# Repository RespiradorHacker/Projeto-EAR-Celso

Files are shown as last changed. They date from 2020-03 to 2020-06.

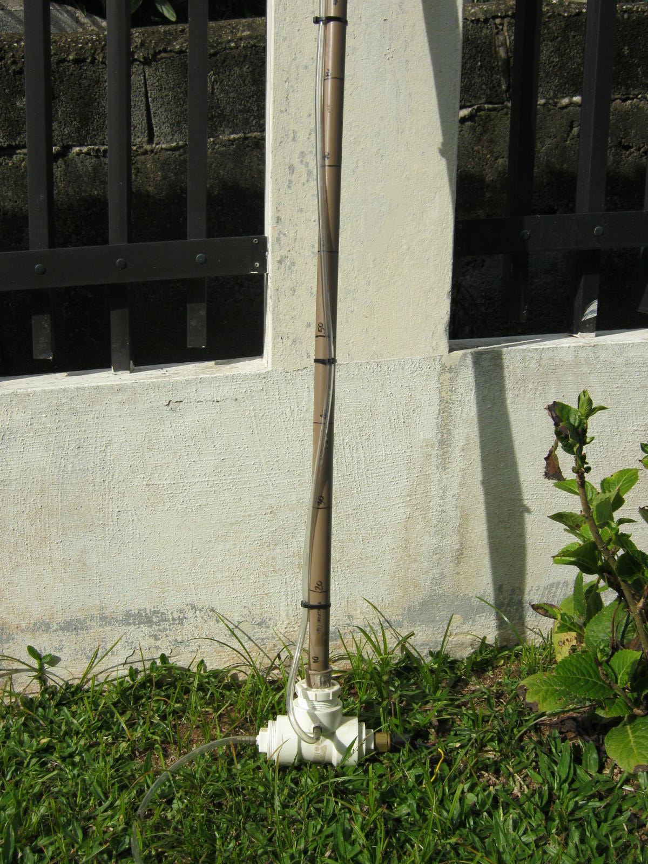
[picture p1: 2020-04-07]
PhotosAndVideos/200407 09.00 Px Sensor Calibration.JPG

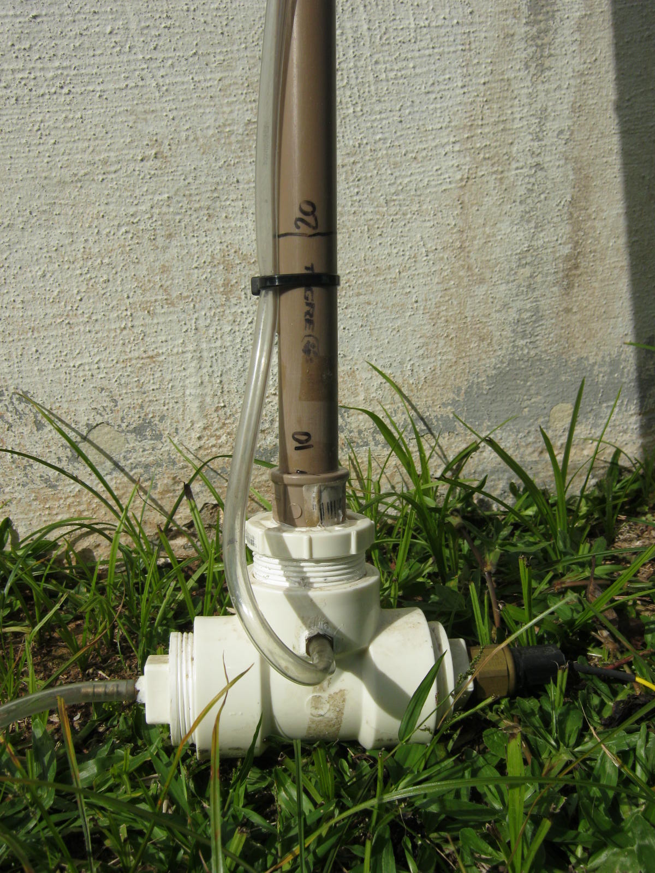
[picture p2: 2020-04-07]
PhotosAndVideos/200407 09.00 Px Sensor Calibration Detail.JPG

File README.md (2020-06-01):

# e-AR (EAR) PROJECT - EMERGENCY VENTILATOR
This project was born because of CoVid19 pandemic.
The project Goal is to provide an emergency ventilator system to help CoVid19 serious cases using locally available resources. eAR was designed to meet specifications according to MHRA (UK) - Rapidly Manufactured Ventilator System and inspired by MIT E-Vent (USA) concepts and specs.

This is an OPEN HARDWARE - OPEN SOURCE PROJECT. 

DISCLAIMER: we will NOT take any responsability on devices built using partial or total information from this project. 
Any device used for life support and medical applications must meet all local requirements and they must be homologated by local regulatory agencies in ANY case.

The target is to run an entire ventilation system using an automotive car battery and an O2 can.
The initial project leader is Celso Ken Mori Monteiro, automotive designer with +30 yrs experience on automotive embedded systems
as OEM designer for customers as GM, Ford, VW, Fiat, Mercedes Benz, Scania, Navistar, Marcopolo, Agco...

The technology for first PCBs was downsized due to components availability in emerging countries so distributed production could be achieved even in small brazilian towns. The electronic parts are:
- PTH components
- Single-sided PCB, obtainable even by DIYs. 

Besides inclusive concept there is also a FR4 SMT version available for volume production.

Basic concepts:
- External FIO2 O2 + AIR mixer based on timed mechanical truck air valves and plastic bag container
- AMBU smasher based on car window motor due to availabilty and great mechanical characteristics. Motor reversion is necessary to allow dinamic changes of BPM, Tidal Volume, pressure ramping, I/E Ratio and Plateau Hold Time without ANY mechanical change.
- ECU based on Arduino Pro Mini (the most available in emerging countries) and SPI based IO expension
- 2 motor drive options: relay (need second adjustable supply or buck) and PWM driven mosfet driver

Project Evolution:
- full HW schematics and system component's description available on "EAR System Developer's HW Guide", portuguese only version
- PCB Gerbers available, Single Side PTH version, Motor driver on relay option only. Time and size were underestimated because we no longer use these old technologies. Released on March 30, 2020.
- Mech prototype phase 2 aproved, torque is OK and current is low.
- Gerbers of single sided boards on PTH components published on March 30, 2020. Time and size were underestimated because we no longer use these old technologies. 
- EAR System Developer's SW Guide released on March 30, 2020.
- Functional electronics prototype built and delivered on April 2, 2020. No changes in PCBs are necessary except hardware end-of-courses provided for EAR ECU Motor Driver Board. Test driven by firmware FW00 - focused on HW testing only. Reads input pots, control motor with reversal action, measures motor current and tests IO expansion board. All items are functional.
- FW00 published in April 3, 2020.
- Added Mosfet-based PWM Motor Driver and Absolute position sensor using a car fuel level sensor.
- First working mechanical+electrical prototype delivered in April 6, 2020.
- Added Pressure Sensor in April 7, 2020. First artificial lung is a balloon so first pressure profile was obtained. It Sounds promising.
- Firmware controls Tidal Volume and BPM according to Set Potentiometers. First functional firmware produce variable pressure ramps as needed, FW met 8-30 BPM dynamic range specification.
- Added motor cutoff in inspiratory phase according to pressure preset on pot Overpressure Threshold within 1cm H20 resolution.
- Added full mechanical design for functional AMBU compressing ARM in April 11, 2020
- Added in April 12, 2020: Motor Driver, mosfet NN version. Full Kicad design with schematics, PCB and Gerbers.
- Added in April 12,2020: eAR External watchdog Timer to increase eAR reliability. Full Eagle design with schematics, PCB and Gerbers.
- Added in April 13,2020: I/E selection (1:1, 1:2, 1:3 and 1:4) and Plateau Hold Time selection (150, 250, 500 and 1000ms hold on Plateau)
- Added in April 13,2020: Gol G3 tank level float sensor added as absolute position sensor. Increased linearity, resolution and availability
- Mech proto 3.2 added ball bearing in compression arm, currently performing cycling tests
- Added in April 15,2020; eAR Pressure sensor Board Design and PCB, MPX5010DP supported
- Added in April 21,2020: 10x10cm FR4 SMT single PCB design for volume production, verified design, send to production
- Added in April 21,2020: Mechanical proto 3.2 drawings delivered, functional design
- April 30, 2004: eAR FR4 Single-Board PCBs arrived, courtesy from Digicart/SC
- May 1st, 2020: eAR system reached 14 days of 24/7 operation, with 403,412 beathing cycles completed. eAR met minimum durability MHRA (UK) Spec with a prototype built on MDF, a window lift BDC motor and a 20-yrs-old chevy tank float sensor
- May 5, 2020: Multiple pressure sensor added, allowing almost any kind of linear pressure sensor to be connected to eAR system, including MPX5010, MPX10 almost all versions and packages including MPVZ and MP3V and experimental ultra-low-cost MPS20N0040D-S sensor
- May 12, 2020: Integrated EAR ECU tested, functional test OK. Some minor drilling errors corrected, some improvements done and new PCB generated. New mosfet driver option added in firmware as needed. Some components changed values due to standardization effort to ease production. eAR electronics is ready for mass production.
- May 23, 2020: Added first steel based eAR mechanical design, by Ricardo Suzuki. Arm sensor changed to DS 1901 non-contact TPS. 
- June 1st, 2020: Added R2 of mechanical design in two verions, geared arm and 4-linked-bars by Ricardo Suzuki

Pending:
- Software reliability improvements.
- Assisted Ventilation Firmware on hold. It can delay ANVISA aproval when requested.

Special thanks to all people that made this project real!
It's impossible to list all names involved, I apologize for forgetting someone.
The partial list follows:

Project Contributors, as they have joined this project
- Joannes Berque (FR): first design idea.
- Celso Monteiro: eletronics and firmware design, system conception and documentation.
- Diego Padilha and Lucas Pianizzer: electronics and mechanical design+prototyping. 
- Marcelo Pires: electronic CAD, schematics capture & PCB Design.
- Nicolai Rutkevich: mechanical concepts.
- Bruno Afogliatto: decontamination concepts.
- Gustavo Ortenzi: motor drive alteratives.
- Ricardo Suzuki: system concepts and mechanical design.
- Rodrigo Azevedo: organized Github Project.
- Douglas Esteves: interface with other projects.
- João Cardoso and Leonardo Afonso: Kicad Capture for Open Hardware.
- Andre Novelli e Victor Acioly: AMBU bags replacement.
- Flavio Alves: GUI design
- David Loos: electronics assembly

References:
- MIT E-Vent: human requirements and system conception ideas.
- MHRA (UK) Rapidly Manufactured Ventilator System

Healthcare professionals involved:
- Angelica Mammana M.D. helped stablishing specs and performed crytical analysis.
- Fernando Machado M.D. was the first contributing doctor.
- Lucio Flavio M.D.
- Ana Teresa Gama.

Project supporters:
- Fabio Knihs.
- Norberto Tomio.
- Gabriel Casagrande.
- Ivandro Ceccato.

Thanks to my family, special thanks to my dear wife Tissa and my children Joana, Gustavo and Leonardo, for their unlimited support and to all the people that prayed for this project, and God that inspired and guided me all the time.

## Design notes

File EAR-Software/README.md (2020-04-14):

# e-AR (EAR).

Open-source Software that runs on e-AR Project MCU. 
- eAR was designed to meet specifications according to MIT E-Vent (USA) and MHRA (UK) - Rapidly Manufacuted Ventilator System.  
- Provides basic functions to human ventilation.
- Runs on e-AR Hardware, Arduino based, functionally available and published as Open Hardware.
- Always use the lastest available software, just download the folder and use Arduino IDE

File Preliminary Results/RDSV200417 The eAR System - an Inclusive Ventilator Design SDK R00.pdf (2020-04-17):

Doc.: RDSV200417 The eAR System - an Inclusive Ventilator Design SDK R00.doc | 1/11

_____________________________________________________________________________

| Data | Signatures
Author: Celso Monteiro | 17/04/2020 | | Títle: The eAR System – Ventilator SDK
Verif.:

Aprov.:

### 1. Scope

The scope of this document is to describe the creation of the eAR system. The eAR system is a low-cost SDK for inclusive ventilator systems developed in around 30 days during the CoVid19 pandemics by a self-funding voluntary multidisciplinary team in Brazil. We’ll present the design alternatives, choices, results and limitations, focused on AMBU automation. This is far from being the best system but it’s the best we can do now on what we have available.

All electronics hardware, mechanical, and software documents are available in open hardware, open software basis in the Githut https://github.com/RespiradorHacker/Projeto-EAR-Celso

This design can be changed at any moment without previous announcement.

Disclaimer: we have no responsability about any device built upon information from eAR project and we emphasize that devices must be built in strict compliance to local regulations, following expert recommendations and they must be homologated by local regulatory agencies.

### 2. Document Control

- April 17, 2020: Document emission R00

### 3. References

- Open Source COVID19 Medical Supplies facebook: https://www.facebook.com/groups/670932227050506/
- COVID-19 Air BRASIL - Fast production of assisted ventilation devices https://www.facebook.com/groups/235476464265909/
- RDSV200320 Emergency Automatic Respirator Specification R00 – Preliminary
- RDSV200322 EAR Hardware Proposition Draft R00 – PTBR
- RDSV200327 EAR Project Briefing PTBR R04
- MIT E-Vent – “Key Ventilation Specifications”
- MHRA (UK) Rapidly Manufactured Ventilator System

### 4. Abbreviations and Terms

- MIT: Massachusetts Institute of Technology (USA)
- MHRA: Medicines & Healthcare products Regulatory Agency (UK)

Doc.: RDSV200417 The eAR System - an Inclusive Ventilator Design SDK R00.doc | 2/11
- AMBU: in this scope is just a silicone bag
- BDC: Brushed Direct Current
- FIO2: Fraction of Inspired O2 defines proportion of O2 in inspired air
- ECU: Electronic Control Unit
- PEEP: Positive End Expiratory Pressure
- PTH: Plated Through Hole, electronics technology
- SPI: Serial Peripheral Interface
- WIP: Work in Progress
- SDK: system development kit

### 5. Design Reasons

There are several AMBU automation solutions, why do we need another one? All AMBU automation we could find are based on materials available in research labs. These materials were not found normally in emerging countries like Brazil and especially on the worldwide uprising of Covid19. Detours on purchasing are announced in a daily basis for all resources targeted to fight Covid19.

So eAR basic concept is creating a system that could be built using available components and local resources. It should be a possibility for any town, including small towns in emerging countries.

### 6. eAR Design - Hardware

The AMBU bag was the enriched air propeller chosen because it was available at all places, used by emergency medical care worldwide.

We needed something to compress the AMBU so at first we were considering an indirect compressed air based AMBU compressing device but this solution needed a dedicated chamber, more complicated to build and we considered that some small hospitals had few available spots of compressed air.

So we switched to electric motor possibilities. There are many alternatives that could do the job, we’ve considered NEMA type stepper motors, car windshield and car window motors. We had previous experience with all three motors. NEMA motors are the only brushless option, but we discarded because of availability in smaller towns. Windshield motors were discarded because they are power hungry, heavy and they were not built to reverse operation. We needed reversal because we wanted to control Tidal volume without mechanical changes. Car windows were the most available (up to 4 on each car and million cars spread through the country) and they had excess torque, low power consumption and reversal capability. There’s a life limit associated with this choice, although these motors work on worm gears and they have rubber couplers, they are brushed motors, and they wear. Due to low load condition we’ve estimated around 1 million cycles (to be confirmed). Possibly it’ll last longer than the AMBU.

Doc.: RDSV200417 The eAR System - an Inclusive Ventilator Design SDK R00.doc | 3/11

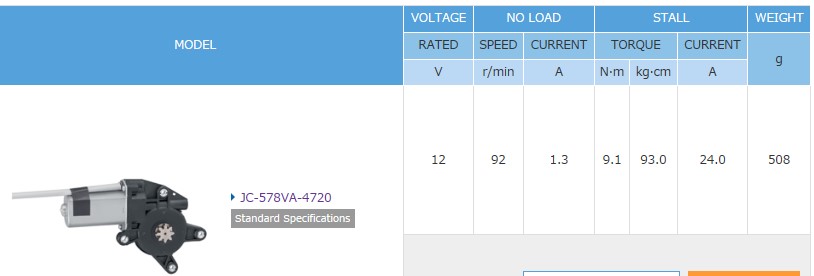
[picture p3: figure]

Motor used in eAR system

We’ve built mechanical prototype 1, it was similar to an Israeli prototype, with direct traction compression arm. It was brute and hard to control. We’ve changed to mechanical prototype 2, this model used the window mechanism original pulleys and steel cable. It was controllable but the steel cable needed to be kept tight, turning it mechanically complicated. The mech prototype 3 introduced gears between the arm and the motor gear with approximately 1:4 reduction. It worked smoothly even under 3V and so far we’ve been enhancing this model.

At some point between mechanical prototype 2 and 3, we started to stablish preliminary specifications. Since the beginning MIT E-Vent design was inspiring, but we found the MIT specs were insufficient. So we found Rapidly Manufactured Ventilator System from MHRA (UK) and we considered it as the main specification. The eAR design now had a main spec: MHRA and a pathway: MIT E-Vent.

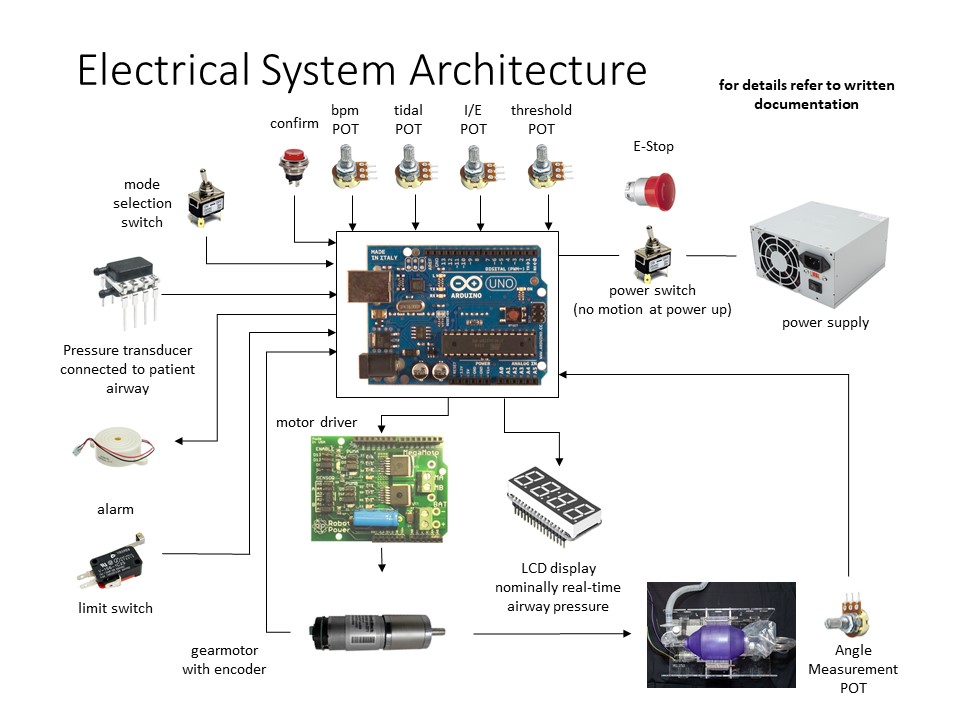
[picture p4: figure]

E-Vent Hardware Architecture

Doc.: RDSV200417 The eAR System - an Inclusive Ventilator Design SDK R00.doc | 4/11

Why we did not use the MIT as is? MIT E-Vent was nice, but the BDC chosen motor was not available here. MIT motor has encoder and planetary gears, and locally available planetary motors use tiny plastic gears which could be unreliable in this application. There were no schematics or lines of code. So we adapted eAR hardware to what we could afford.

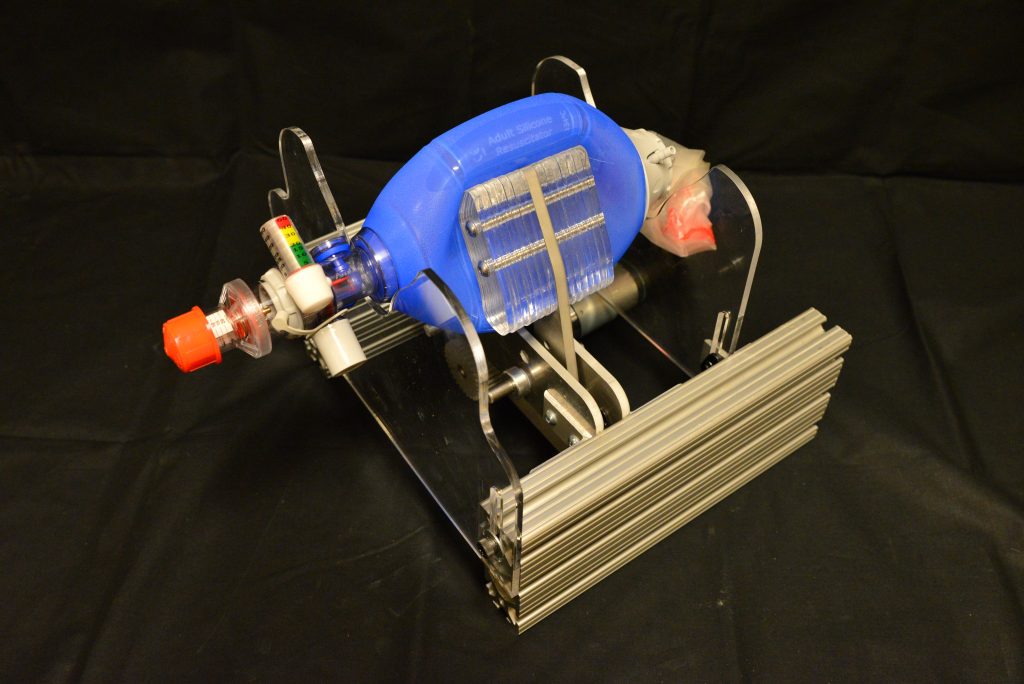
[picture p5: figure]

MIT E-Vent Ambu Compressor

We’ve kept the 4 potentiometers of MIT Design, added failsafe resistors for failure mode open when operating. We replaced I/E for Assisted Pressure Threshold on pot, according to MIT recommendation.

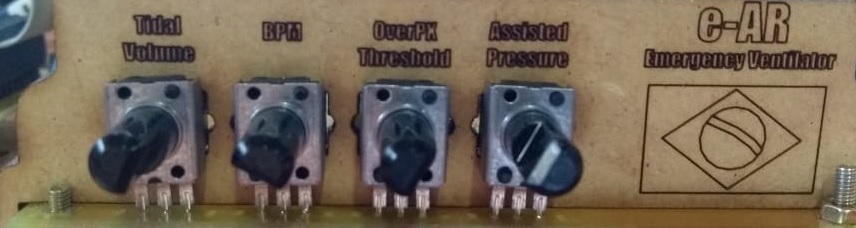
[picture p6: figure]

eAR prototype front panel main controls

We did not use MIT display because we do not consider 7-segment displays adequate for instant visibity, so we depend on external pressure viewer which could be an electronic bargraph panel, a mechanical set or a GUI, currently being developed.

About the MCU, we chose Arduino Pro Mini due to availability and small DIP24 footprint. We are not 100% sure that Arduino will meet all reliability issues so we added some extras to improve reliability like some ESD protection and an external hardware watchdog timer. If Arduino ultimately fails validation, we can provide a PCB with another processor using Arduino’s DIP24 footprint.

We were not able to find an available superb quality angle measurement pot as MIT did. So we started using a revolution sensor and end-of-course to read AMBU compressing arm position. But motor speed changed according to arm travel and effort. So we’ve introduced a car tank float sensor as an absolute arm position sensor. I’ve designed in nineties the production tester for the GM Corsa tank float sensor for Indebras, so we know the sensor and the failure modes. Although

Doc.: RDSV200417 The eAR System - an Inclusive Ventilator Design SDK R00.doc | 5/11

the Corsa sensor was over 20 years old, it worked flawlessly. These sensors usually fail open so it’s easy to notice intermittent failures so we can replace sensors before catastrophic failure. In order to avoid problems with this type of sensor, we recommend observing the curve of the sensor during movement. In poor quality sensors, it is easily noticed flatness at some points, this is due to grey sensor manufacturers “enhancing” carmakers checkpoints (e.g 1/4, ½, ¾) In mechanical prototype 3.1 we’ve upgraded to Gol G3 sensor, with increased resolution and linearity.

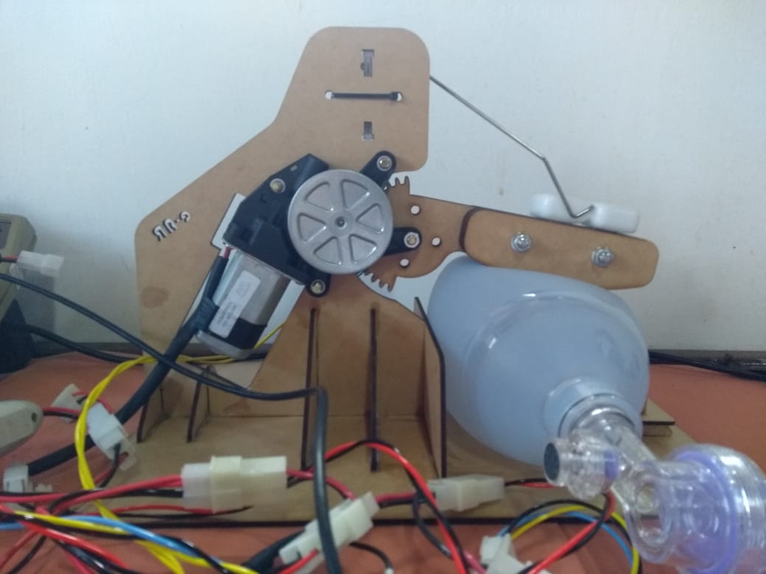
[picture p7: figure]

eAR mechanical prototype 3.1 mounted with MDF parts

We’ve directly correlated the Arm position Sensor with Tidal Volume because the arm displacement is related to Ambu compressing and it will tell the possible maximum displacement of enriched air for the patient. This is a restriction on eAR system, at least for now it does not measure airflow to pacient, it will only estimate the real quantity of dispensed air. This was done in order to keep system costs down because a reliable flowmeter would be the most expensive part of eAR system. If necessary we can review it, maybe using a custom built hot wire flowmeter. Our expectation is that the necessary Tidal volume will be set by the healthcare professional turning the Tidal volume knob clockwise and observing the patient chest cavity displacement. Other drawback from not using a flow sensor is that some asynchronies during assisted ventilation will be harder to identify, maybe we’ll miss some of them.

Doc.: RDSV200417 The eAR System - an Inclusive Ventilator Design SDK R00.doc | 6/11

Regarding the motor driver, we could not identify an available PWM H-bridge motor driver. There are popular drivers based on L298 but they are not specified to handle the 7-8 Amps peak motor current during motor start. We finally developed two driver versions: first model is a relay based motor driver that does not use PWM and you have to add an external power supply or a variable DCDC converter to set motor speed. The second model is a Mosfet based PWM that allows dynamic motor control. The design allows you to use any TO220, DPAK or D2PAK low level drive N-Channel mosfet that meets the current and voltage specs.

There are currently 2 versions of printed circuit boards: the first version is the inclusive one. It is a set of 3 PCBs, 10x10cm, single sided with PTH components. Anyone can buy the shelf 10x10cm copper PCB, use a DIY PCB method and get the boards done. The connections between the boards are handled by IDC Flat cables, with retundant vias to increase reliability. These flat cables can be obtained even on old PC floppy cables. We’ve downsized technology to allow this inclusive design. POC proved it works!

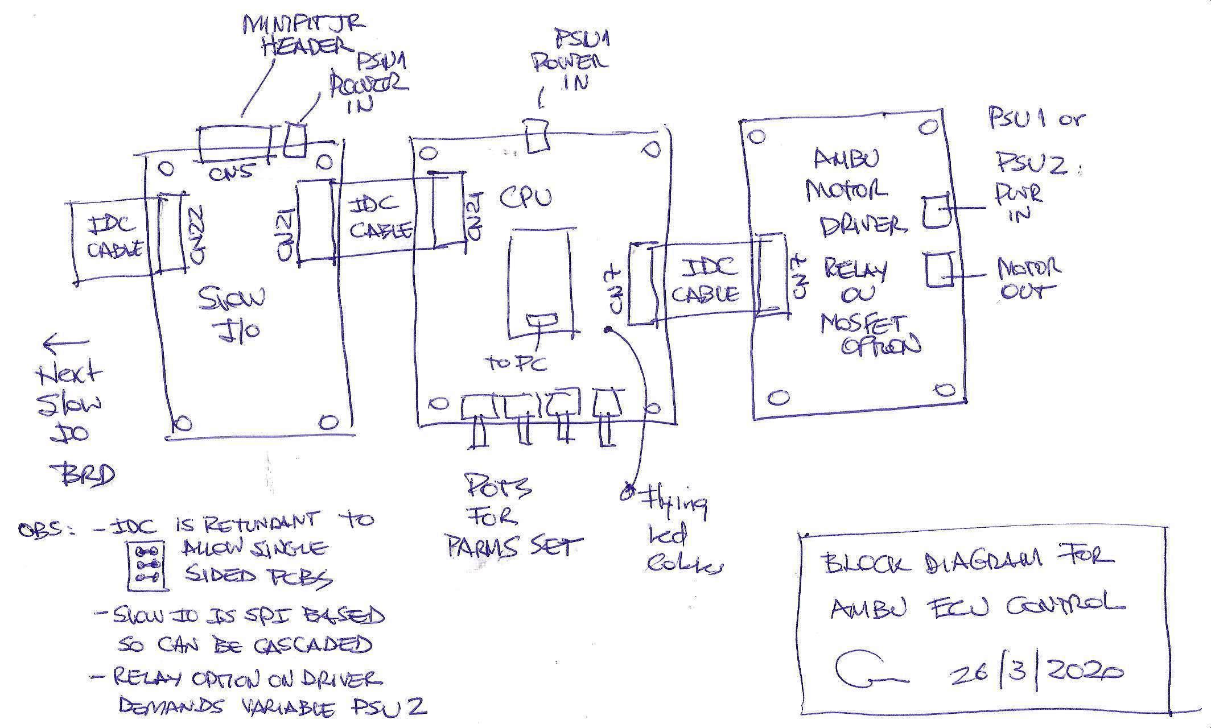
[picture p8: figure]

Early Inclusive version sketch

The second PCB version is a single 10x10cm FR4 board SMT version. This alternative allows higher volume production.

We used a standard 5V pressure sensor, NXP MPX5010, with 10 KPa sensivity but any sensor working on a range of 5-70cm H2O will work. This sensor is linear, so the resolution depends on the ADC we’re currently using. The manufacturer’s spec for pressure precision is 5% but we’ve achieved less than 1% precision in previous designs based on 2-points calibration procedure. This calibration procedure is very simple: we build some calibrated tubing, place the sensor in a stardard position regarding the water column and use the system to read raw readings of 2 points, e.g. 5 and 40 cm H2O. With this readings we enter raw readings as parameters on a provided Lookup Table Generator software (based on Arduino too in order to avoid extra software) so we have a now 2-points calibrated curve. We’ve got precision better than 1 cm H2O.

Doc.: RDSV200417 The eAR System - an Inclusive Ventilator Design SDK R00.doc | 7/11

We also added some extra IO to eAR so we could read external switches and drive directly 12Vdc loads, e.g external relays or light loads. We used SPI interface so the expansion is modular based on 8 Inputs/8 Outputs base module. Using 4 of these inputs we already implemented I/E Ratio and Plateau Hold Time selection.

Mode selection switch is directly connected to Arduino. This switch defines forced mode or assisted ventilation.

Status as April 17, 2020:

- Inclusive eAR hardware (PTH single sided boards):
- eAR ECU CPU Board: designed, tested, works
- eAR ECU I/O Expansion Board: designed, tested, works.
- eAR ECU Motor Driver Board – relay option: designed, tested, works. Rework required to handle arm sensor (added later) and changed HSA and LSB signals. Recommended use of Mosfet driver instead due to best performance and no extra PSU.
- eAR ECU Motor Driver Board – mosfet option: designed, electronics works, untested PCBs.
- eAR Pressure Sensor board: designed, electronics works, untested PCBs
- eAR watchdog Timer Board: designed, electronics works, untested PCBs
- eAR hardware for mass production (FR4 SMT boards):
- eAR ECU (CPU + IO + Mosfet motor Driver + watchdog Timer) expected release this week: designed, electronics works, untested PCBs
- eAR Pressure Sensor board: designed (PTH), electronics works, untested PCBs

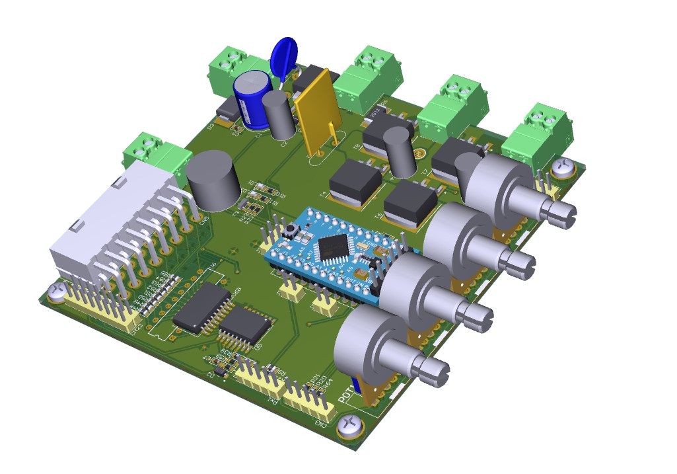
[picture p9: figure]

eAR Hardware for mass production – 10x10 cm Single Board SMT solution

Doc.: RDSV200417 The eAR System - an Inclusive Ventilator Design SDK R00.doc | 8/11

### 7. eAR Design - Firmware

Arduino is a platform for learning embedded systems, with a nice IDE and one of the largest base of developers. It is not really a reference for real time designs. In order to implement the real-time needs for eAR, we proposed a very simple software architecture.

This architecture is based on an interrupt based timer, that generates the system timebase, which is currently 10ms.

We established an eternal loop like PLC software, and we added a deterministic task scheduler, or task sequencer. So we basically have one part of the firmware that runs every 10ms and 10 tasks that execute every 100ms.

Notice that the tasks are not dynamically created, there is no RTOS structure or anything that could be stack or processing time intensive. This is a tiny 8-bit processor, there are no resources for that. Flash footprint is 32KB and so on.

Final arm position is tightly correlated to Tidal volume potentiometer so arm course is directly proportional to Tidal pot position.

BPM pot is translated into 8-30 BPM according to MIT proposed math functions. Total breathing period takes into account I/E ratio, inspiration time, plateau hold time and expiration time. All of them are variables. I/E ratio and Plateau hold time are switch setpoints, inspiration and expiration time are calculated from BPM, I/E ratio and Plateau hold time.

Float processing is avoided, notice that the Arduino MCU cannot even handle 16/8 division on hardware. Most math are handled using integer processing, sometimes lookup tables.

Software changes PWM in order to change pressure ramping speed according to inspiration time set.

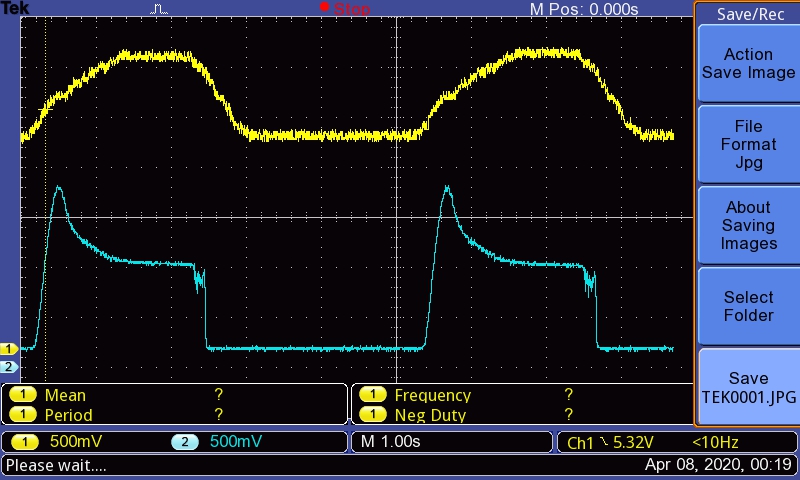
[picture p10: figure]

First pressure profile

Doc.: RDSV200417 The eAR System - an Inclusive Ventilator Design SDK R00.doc | 9/11

This is the first registered pressure profile. In yellow we see the arm position sensor and in blue
we see the pressure sensor signal. The high peak – plateau delta is due to we were using a baloon and there is a negative resistance area on pressure using these devices. The pressure went down
to zero because there was no PEEP valve in this setup.

Maximum inspiration pressure is programmed by Overpressure threshold pot. If this threshold is set, eAR stops motor from pushing. Results are lower than 1 cm H2O.

External watchdog must be disconnected in order to reprogram the Arduino MCU. eAR hardware provides that if watchdog is disconnected the software can recognize it.

FiO2 was excluded from eAR scope because we could assemble a single FiO2 central for supplying enriched air for several eARs so we’ve decided to start a new independent design.

There is no Peep Control, it must be handled externally. We’ve found this inclusive alternative from Cincinnati Children Hospital that is called a Bubble Peep. You can control Peep pressure moving the tube up and down and even start decontamination phase if you put soap on the water. It’s well known that soap adheres to Covid19.

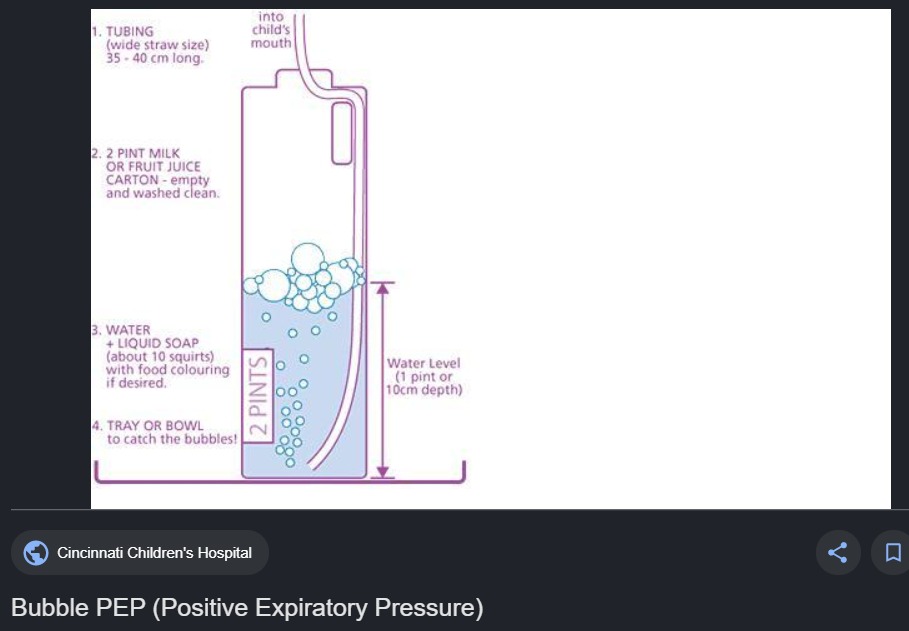
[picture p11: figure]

Status as April 17, 2020:
- Implemented all functions necessary for forced mode ventilation, using 18% of MCU flash footprint and 31% of Ram footprint.
- Assisted mode is a work in progress

Doc.: RDSV200417 The eAR System - an Inclusive Ventilator Design SDK R00.doc | 10/11

### 8. eAR GUI

Status as April 17, 2020:

- Under development, WIP

### 9. eAR Design – Preliminary Results

Preliminary results of eAR system:

- Preliminary BOM under USD 90, including ECU electronics, mechanical compressor arm and pressure sensor.
- Airway pressure measurement resolution and precision: 1 cm H2O
- Overpressure threshold resolution and precision: 1 cm H2O
- Airway pressure controlled cutoff: less than 1 cm H2O over programmed threshold
- BPM timings errors are unnoticeable. Range: 8-32 BPM
- Tidal Volume: 200-800ml range, 2 ml resolution, undetermined precision, expected repeatability 5%.
- Plateau Hold Time: 150, 250, 500ms and 1s, switch selectable.
- I/E ratio: 1:1, 1:2, 1:3 and 1:4, switch selectable.
- Power consumption: less than 10W@12V per eAR system
- Motor PWM range: 0-100%, 1% resolution.
- FiO2 is externally set. A single unit can feed several eAR systems. In a severe crisis scenario we can run several systems using a single O2 pressurized bottle and a 12V battery with a charger.

### 10. eAR Project – Partial list of the Design Team – Thanks

Project Contributors, as they joned this project
- Joannes Berque (FR): first design idea.
- Celso Monteiro: eletronics and firmware design, system conception and documentation.
- Diego Padilha and Lucas Pianizzer: electronics and mechanical design+prototyping.
- Marcelo Pires: electronic CAD, schematics capture & PCB Design.
- Nicolai Rutkevich: mechanical concepts.
- Bruno Afogliatto: decontamination concepts.
- Gustavo Ortenzi: motor drive alteratives.
- Suzuki: system concepts.
- Rodrigo Azevedo: organized Github Project.

Doc.: RDSV200417 The eAR System - an Inclusive Ventilator Design SDK R00.doc | 11/11
- Douglas Esteves: interface with other projects.
- João Cardoso and Leonardo Afonso: Kicad Capture for Open Hardware.
- Andre Novelli e Victor Acioly: AMBU bags replacement.
- Flevio Alves: firmware design
- David Loos: electronics assembly

References:
- MIT E-Vent: human requirements and system conception ideas.
- MHRA (UK) Rapidly Manufactured Ventilator System

Healthcare professionals involved:
- Angelica Mammana M.D. helped stablishing specs and performed crytical analysis.
- Fernando Machado M.D. was the first contributing doctor.
- Lucio Flavio M.D.
- Ana Teresa Gama.

Project supporters:
- Fabio Knihs.
- Norberto Tomio.
- Gabriel Casagrande.
- Ivandro Ceccato.

Thanks to my family, special thanks to my dear wife Tissa and my children Joana, Gustavo and Leonardo, for their unlimited support and to all the people that prayed for this project, and God that inspired and guided me all the time.

Celso Ken Mori Monteiro, April 17, 2020.

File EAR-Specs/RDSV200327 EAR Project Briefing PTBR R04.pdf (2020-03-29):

Doc.: RDSV200327 EAR Project Briefing PTBR R04 | 1/5

_____________________________________________________________________________

| Data | Signatures
Author: | 27/03/2020 | | Títle: Descritivo Simplificado Projeto EAR Preliminar
Verif.:
Aprov.:

### 1. Escopo

O objetivo deste documento é apresentar o projeto EAR de forma simplificada. Este projeto nasceu no grupo internacional CoVid19 e se trata de um sistema INVASIVO que utiliza um AMBU somente para propulsão do ar para o paciente, ou seja utiliza somente a estrutura mecânica do AMBU. O sistema permite controle da compressão do AMBU, permitindo variação da quantidade de ar inspirado, quanto da pressão máxima aplicada, frequência de operação e outros parâmetros, programáveis por potenciômetros. O projeto está sendo realizado para atender aos requisitos do projeto do MIT E-Vent – “Key Ventilation Specifications”

O projeto EAR vai disponibilizar de forma aberta tudo o que é necessário para obter e construir os componentes necessários para ter um sistema operacional, utilizando componentes de fácil obtenção ou construção. Um exemplo é a utilização de motores de vidros de carros de passeio, que já se comprovaram excelentes para comprimir os AMBUs.

Estão previstas ampliações de escopo do projeto para suportar respiração assistida, Somente para os pacientes em fase de recuperação. A eletrônica do projeto EAR já contempla expansões para esta função e outras. Este projeto pode ser alterado a qualquer momento, sem aviso prévio.

Disclaimer: não assumimos nenhuma responsabilidade sobre qualquer dispositivo construído a partir das informações deste documento e orientamos para que os dispositivos sejam projetados na estrita observância às normas locais, que sigam as recomendações de especialistas e que sejam homologados pelas agências reguladoras em todas as fases.

### 2. Controle do Documento

- 21/03/2020: Emissão R00 – Português BR
- 22/03/2020: Release R01 – English
- added slight helmet pressure for PEEP effect
- added decontamination possibilities
- added adult model in AMBU type
- 23/03/2020: Emissão R02 - – Português BR
- adicionadas melhorias da R01 em inglês
- adicionada caracterização do EAR como um produto que utiliza somente a mecânica do AMBU
- adicionada descrição de alguns dos parâmetros controlados
- adicionada reversão de motor para possibilitar controle da quantidade de ar
- adicionada alimentação por fonte DC

Doc.: RDSV200327 EAR Project Briefing PTBR R04 | 2/5
- explicitada capacidade de expansão para respiração assistida
- explicitada necessidade de reversão do motor

-23/03/2020: Emissão R03 – Português BR
- explicitada que se trata de uma técnica INVASIVA e que o AMBU é um componente mecânico apenas de um sistema de rspiração controlada
- revisto e explicitado o escopo para facilitar o entendimento do projeto
- removido nome do autor, porque se trata de um projeto coletivo e colaborativo

-26/03/2020: Emissão R04 – Português BR
- definição de componentes adicionais
- melhorado o desenho (by Suzuki)
- adicionado aderência aos requisitos E-Vent
- detalhado funcionamento do processo
- adicionado Disclaimer

### 3. Referências

- Open Source COVID19 Medical Supplies facebook: https://www.facebook.com/groups/670932227050506/
- COVID-19 Air BRASIL - Fast production of assisted ventilation devices https://www.facebook.com/groups/235476464265909/
- RDSV200320 Emergency Automatic Respirator Specification R00 – Preliminary
- RDSV200322 EAR Hardware Proposition Draft R00 – PTBR
- MIT E-Vent – “Key Ventilation Specifications”

### 4. Descritivo Simplificado do Projeto

Existem várias soluções de automação de AMBU, porque mais uma? A razão é simples: todas as automações de AMBU foram baseadas em materiais de disponibilidade em centros de pesquisa, não em municípios de menor renda. Sim, os 60% de municípios brasileiros que não dispõem de ventilador mecânico provavelmente não disporão dos insumos para produzi-los ou mantê-los neste primeiro momento.

O foco então se trata de um equipamento para regiões sem recursos, principalmente em países emergentes. Trata-se então do já difundido conceito de ter uma mão mecânica para apertar um AMBU. Atenção: houve alteração no modo de acionamento em relação a especificação original que era pneumática porque ar comprimido não está disponível em muitos locais de saúde.

Esta mão mecânica é composta de um mecanismo de compressão mecânico movido por um motor de máquinas de vidro de automóveis, que já conhecemos e utilizamos em escala em produtos. Conhecemos os modos de falha do motor e os estamos tratando. O motor de vidros tem mecânica adequada para suportar reversões em cada ciclo, necessárias para o controle da quantidade de ar e da pressão aplicada ao paciente.

Doc.: RDSV200327 EAR Project Briefing PTBR R04 | 3/5

Para o controle do sistema foi desenvolvida uma placa de controle que pode ser montada e construída por qualquer pessoa que fabrique artesanalmente equipamentos eletrônicos, a ECU EAR. A placa de circuito impresso está sendo projetada como face simples, para que possa ser produzida até por processos artesanais. Para alteração dos parâmetros, esta placa tem controles por potenciômetros para permitir uso fácil pelos profissionais de saúde. O microcontrolador é um Arduíno, similar ao da solução do MIT, que tem a maior base de desenvolvedores no mundo. Esta placa tem várias proteções, inclusive contra curto-circuito no motor, que entra em curto após uso prolongado. Esta placa também controla a velocidade do motor, definindo a pressão aplicada no AMBU. O uso do motor é reversível, para possibilitar o controle de deslocamento de compressão do AMBU, permitindo a variação do ar inspirado, ou volume tidal. A placa também possui várias entradas e saídas para acionamento direto de relés e leitura de sensores NPN.

Requisitos básicos a serem atendidos, de acordo com: MIT-KVS: Key Ventilation Specification do MIT

- BPM (respirações por minuto):
- MIT-KVS: 8-30BPM
- Volume Tydal - quantidade de ar a ser administrado ao paciente:
- MIT-KVS: 200-800ml baseado no peso do paciente
- I/E ratio (relação tempo de inspiração / tempo de expiração):
- MIT-KVS: começar entre 1:2, melhor se ajustável entre 1:1 e 1:4
- Pressão máxima:
- limitada a 40cm H2O em qualquer condição, recomendada válvula passiva de alívio fixa em 40cm H2O
- pressão de platô limitada a, no máximo, 30 cmH20
- PEEP é necessário de 5-15 cm de H2O, muitos pacientes precisam 10-15 cm de H2O

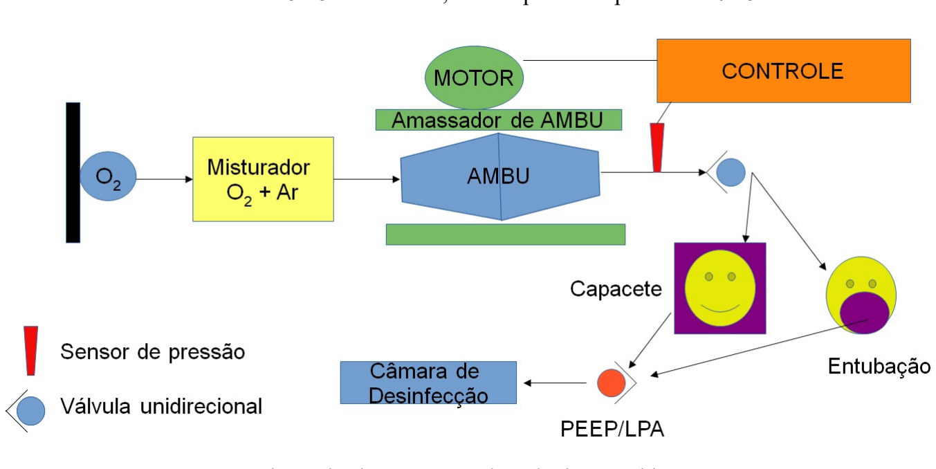
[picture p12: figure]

Esboço do sistema EAR, desenho by Suzuki

Doc.: RDSV200327 EAR Project Briefing PTBR R04 | 4/5

O processo controlado pode ser implementado da seguinte forma:

1 - Mistura por válvulas mecânicas especializadas ou eletroválvulas pneumáticas a partir de duas fontes: O2 comprimido e ar comprimido. A mistura pode ser controlada pela ECU

2 – Compressão da Bolsa de AMBU ADULTO por um mecanismo motorizado com reversão. O controle de volume Tydal é realizado mediante controle de curso e a pressão máxima é realizada por controle da velocidade do motor. Estamos trabalhando em conjunto com desenvolvedores para termos bolsas para reposição, pois prevemos que estourem pelo uso contínuo. Em caso de rompimento de bolsa, quebra de motor ou dano de algum componente mecânico todo o conjunto compressor de AMBU pode ser substituído em menos de 5 segundos.

3 – Acoplamento ao paciente, método não invasivo: usa máscara de AMBU com válvula unidirecional adicional para evitar retorno ao AMBU do ar contaminado e encaminha para uma câmara descontaminante o ar expirado pelo paciente. Controle de Peep mandatório. Capacete com pressão negativa se disponível. Respiração assistida prevista no escopo do projeto.

4 – Acoplamento ao paciente – método invasivo: nesta etapa está prevista ventilação não assistida com uso de mangueira intratraqueal em pacientes sedados. Haverá monitoração de pressão positiva com alerta para detecção de expiração conflitante pelo paciente.

Utilizamos máscara de AMBU com mangueira e válvula para evitar retorno ao AMBU do ar contaminado e que encaminhe para uma câmara descontaminante o ar expirado pelo paciente. Peep mandatório. Capacete com pressão negativa se disponível.

5 - Controle de PEEP

Haverá controle de PEEP por filtro de barreira HEPA ou similar, associado ou não a uma restrição mecânica para controle de pressão de PEEP. Caso não existe filtro de barreira, será mandatória exaustão ou câmara de descontaminação.

Obs: haverá um medidor permanente de pressão de PEEP, mecânico ou eletrônico.

6 - Exaustão do ar contaminado

Esta etapa será mandatória se o ar expirado pelo paciente não passar por filtro de barreira. Podem ser aplicadas as soluções abaixo isoladamente ou em conjunto.

- Passagem forçada por descontaminantes químicos ou mecânicos. Podem ser utilizadas soluções com sabão, que aderem às gorduras do Covid19, ou água sanitária (fonte abundante de hipoclorito de sódio ou cálcio) em concentrações adequadas.
- Aquecedores por queima. Para submeter o vírus a altas temperaturas. Podem ser utilizadas serpentinas para aquecimento de água onde o ar passaria dentro, usar o ar expirado em chaminés com queima de madeira ou gás, junkers, etc
- Irradiação UV: o Covid19 poderia ser submetido a UV de alta intensidade. Seria necessário um tempo de exposição de muitos minutos mesmo com fontes de alta intensidade

Doc.: RDSV200327 EAR Project Briefing PTBR R04 | 5/5

Todo o setup acima pode ser alimentado por baterias automotivas carregadas pela rede AC, para prover energia mesmo que caia a rede AC ou por uma fonte DC de 12V, 30 ampéres ou maior, destas utilizadas para alimentar iluminação de Leds, encontráveis em casas de eletrônica ou iluminação.

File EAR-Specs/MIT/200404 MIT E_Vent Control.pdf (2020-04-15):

## Controls - MIT E-Vent | MIT Emergency Ventilator

Updated 25 March 2020

This page details the control strategies for the MIT E-Vent. Other control strategies with increasing complexity may be implemented at developer discretion and with clinical input.

Notice: Any control strategy must fulfill the requirements described in Key Ventilation Specifications. The goal of the high-level controller is to provide a controlled volume of air to the patient in a set amount of time. There are two control phases:

the inspiratory phase and the expiratory phase (see Figure 1). There are three input parameters, referencing the Key Ventilation Specifications: Parameters

Tidal Volume (TV): The total volume of air to be delivered to the patient.

BPM: Breaths per minute, also called respiratory rate (RR). Typically varies between 8-30 BPM.

IE Ratio (IE): The ratio of the duration of the inhale to the duration of the exhale. For example, a 1:3 ratio means that the exhale phase lasts three times longer than the inhale phase. Typically varies between 1:1 to 1:3, with a maximum of 1:4 currently being observed in COVID-19 patients.

In addition to these inputs set by the clinician, the high-level controller uses two more inputs: the motor encoder position and the system pressure. Its job is then to translate all these inputs into the motor commands the low-level controller needs: desired motor speed and position.

Note that because our device does not directly measure volume, the tidal volume (VT) input of our controller is specified as a percent of a full compression of the Ambu bag instead of Liters. The percent (%) of bag compression from 0 – 100% maps to the encoder pulses that correspond to how far the fingers of the device move towards or away from each other and this determines the volume of air delivered.

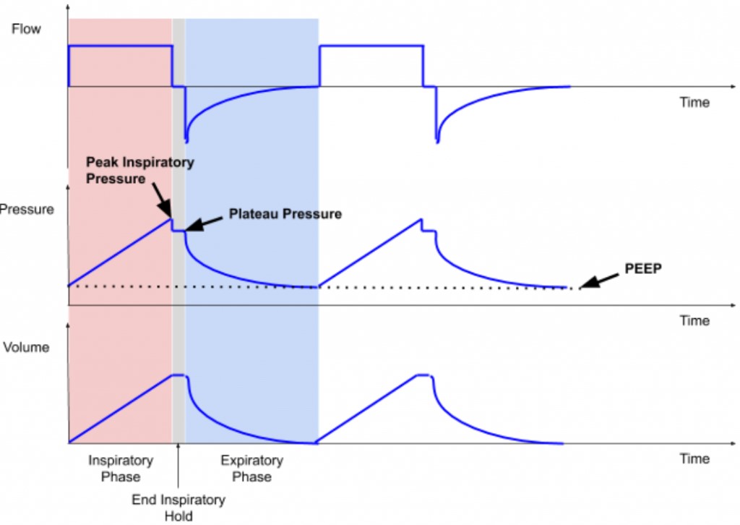
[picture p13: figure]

Figure 1 – Flow, Pressure, and Volume profiles for volume-control ventilation over 2 breath cycles; PEEP is illustrated on the Pressure plot. Image courtesy AK.

Our controller converts the three inputs into four parameters:

Period (T): The length of time (in seconds) of an inhale/exhale cycle.

T = 60 / BPM

Tin: The length of time (in seconds) of the inspiratory phase.

Tin = T / (1 + IE)

Tex: The length of time (in seconds) of the expiratory phase.

Tex = T – Tin

Vin: The rotation rate of the inspiratory phase (in pulses/second).

Controls - MIT E-Vent | MIT Emergency Ventilator | https://e-vent.mit.edu/controls/high-level-controls/
1 of 3 | 04/04/2020 08:35

Vin = VT / Tin

In addition to these four parameters, there are three user-set parameters:

Th: The amount of time (in seconds) to hold the compression at the end of the inhale for plateau pressure.

Ve: The velocity of the fingers in the expiratory phase (in pulses/second). Note that during exhalation, our device does not control flow rate out of the patient. This velocity is simply the velocity of the fingers opening and is not related to expiratory flow rate.

Pmax: The maximum allowable pressure (set to 40 cmH20).

These six parameters are then used to control a state machine that switches between phases in the control loop (see Figure 2).

Time t is the amount of time spent in the current state.

In addition to these three inputs, there are three measurable pressure parameters that must be taken into account (see Figure 2):

Pip: Maximum pressure during inhale. We consider 40 cmH20 to be the upper pressure limit for safety. This also corresponds to the overpressure release valve limit on some Ambu bags.

Pplat: The plateau pressure of the inhale. An important diagnostic number for clinicians.

PEEP: The residual pressure in the system after exhale. We do not directly control this value, but it is typically controlled manually via a PEEP valve on the Ambu Bag.
State Machine Summary

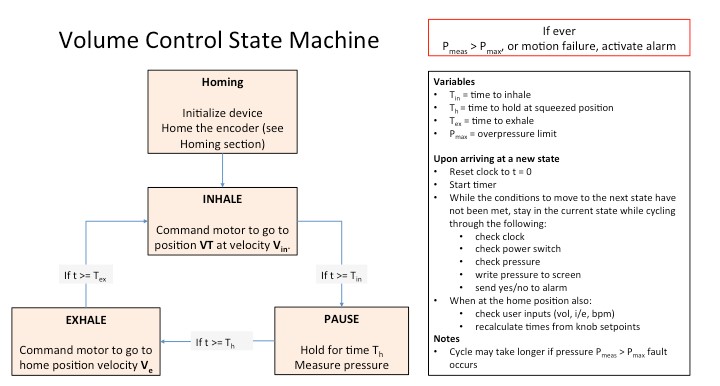
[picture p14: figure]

Figure 2 – State machine for controlling the breathing cycle.

During the setup phase, we initialize the program, start serial communication with the motor controller, and home the encoder.

Figure 3 – We home the encoder using a limit switch.

In the inspiratory phase, we command the motor to go to position VT at velocity Vin. After Tin seconds, we switch to the pause state.

In the pause state, we hold for time Th and measure the plateau pressure. We then switch to the expiratory phase.

In the expiratory phase, we command the motor to go to position 0 at velocity Ve. After time Tex, we switch back to the inspiratory phase.

Plateau Pressure

Each time the arms close, we implement a 0.15 s pause before they open. This does not affect the I/E ratio, but it is necessary to hold the air into the patient. During this phase the airway pressure is measured and displayed. This indicates “plateau pressure” and will guide clinical decision making. This pressure will be displayed until the next cycle and update. Other pressures are less important but can be addressed in a more complicated control strategy.

Alarms Functions

Caution – Not yet implemented. Not all failure modes have been explored yet, so this document will be continuously updated as new faults are found.

All alarms must simply, concisely, and clearly alert the clinician of the type of fault, so that the clinician can decide how to proceed. For example, a mechanical fault requires a different clinical response than a patient who stops breathing on assist mode.

There are several different failure modes in volume control, which require different responses. For example, a compression may cause a lung overpressure fault, or the position setpoint may not be able to be reached.

So far, Volume Control faults include overpressure in the lungs, motor unable to reach desired position, and pressure not increasing when bag is squeezed. This is not a complete list.

In the Assist Control mode, the alarm will also sound whenever a breath is not activated by the patient and the system’s timer kicks in to

2 of 3 | 04/04/2020 08:35

command a breath. Additionally, if pressure does not change when the bag is squeezed, an alarm sounds.

Other alarm conditions will be added. The main goal of all alarms should be to concisely and unambiguously alert a technician that manual intervention is needed. The system should also inform the clinician of the cause of the fault, so that they can act accordingly.
Work in Progress

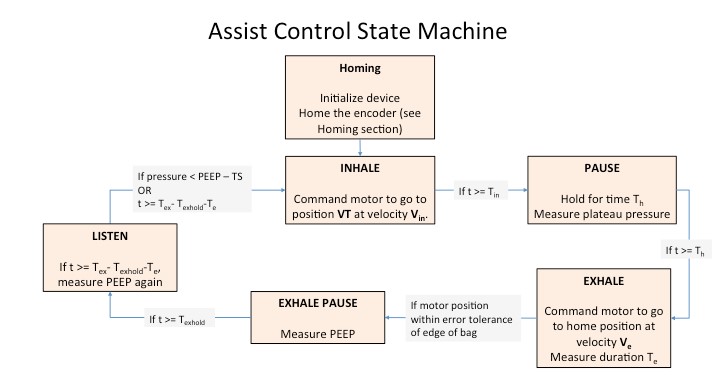
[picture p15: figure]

Figure 3 – Assist Control

Assist Control differs from regular volume control in that the Exhale state is split into 3 states. In the first Exhale state, the fingers move to their home position at the edge of the bag. In the second state, Exhale Pause, the fingers pause for a short time and measure the PEEP. In the third state, Listen, we wait either for the patient’s own inhalation to trigger the Inhale state, or we wait for a set amount of time (like in normal Volume Control) and then trigger the Inhale state automatically.

3 of 3 | 04/04/2020 08:35

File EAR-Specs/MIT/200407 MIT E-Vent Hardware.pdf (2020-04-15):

## Electrical Hardware - MIT E-Vent | MIT Emergency Ventilator

Updated 29 March 2020

Note update on motor specifications and addition of alarm and confirm buttons. This is all key safety information.

This page provides a description of the minimum hardware set required to control the ventilator as described in the other documentation.

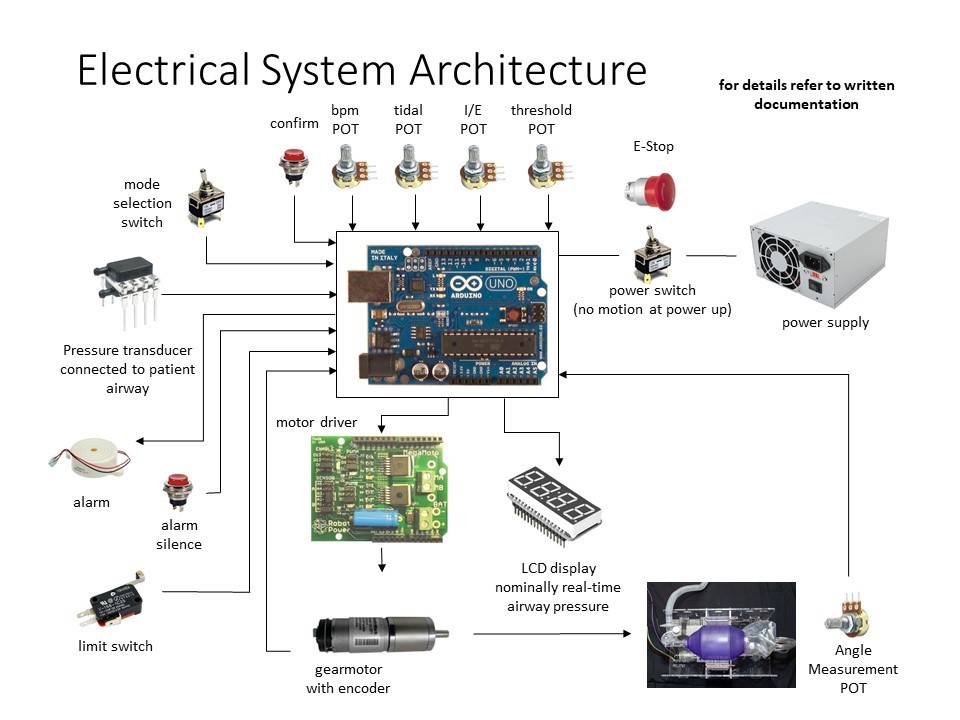
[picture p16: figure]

Motor & Encoder

The mechanical system should be driven with a motor under closed loop control. For feedback measurement, we are using a DC gear motor with integrated quadrature feedback. This is the safest solution.

The beginning point for motor selection should be the Power Calculation based on the force needed to compress a bag.

Motor selection will then vary highly as a function of your geometry and we provide information on Motor Selection, based on our design.
Power Supply

Nominally, a power supply that can deliver 12 V and 5 A is expected to work. Rapid deceleration of the motor causes supply-voltage spikes and must be avoided via correct motor motion profile design. Capacitors should be added across the H-Bridge power leads for extra protection.

An alternate power supply would be to use a car battery with a 5 A car battery charger connected. This will allow for very high instantaneous power draws and voltage spike absorption. The battery will double as a ~2-3 hour backup in case of building power loss. Controller

Microcontroller for timing, measuring, and actuating: Arduino Uno – readily available and easy to program, with extensive online support and documentation. It provides 6 A/D pins (for potentiometers and pressure sensors) and 13 digital I/O pins, including dedicated hardware interrupts (for encoders) and PWM pins for H-bridge driving. Other industry validated controllers can be used, and we may implement them in the future.
Motor Driver

Use any motor driver with sufficient voltage and current ratings to meet the motor power specifications. Closed loop servo controllers can also be employed. Our control strategy is PWM with a H Bridge. For fastest implementation using cheap, off-the-shelf parts, we recommend an Arduino compatible motor shield. More industrial versions will be safer. Main recommended motor controller specifications:

Electrical Hardware - MIT E-Vent | MIT Emergency Ventilator | https://e-vent.mit.edu/controls/electrical-hardware/
1 of 2 | 07/04/2020 19:59

Speed plus position command input that is robust
Accepts quadrature encoder input for closed loop feedback
Has integaretd safety features, including but not limited to, temperature sensing and current limiting that can be communicated to the controller. (What action a fault condition should initiate is not yet defined, ideally this will throw an alarm and message.) Capable of handling up to 15 A. (This is to handle random spikes; you must conduct testing to determine your requirement.)

Caution: Motor controllers can create significant heat inside an electronics enclosure, be sure to consider cooling. Solutions include active cooling with a fan, connection to a protruding heat sink or connection to a large metal chassis.

For reference, we are using a RoboClaw Solo motor controller to control a brushed DC gear motor. The RoboClaw firmware uses a velocity PID controller and a position PID controller to command the motor to a desired position at a desired velocity. The PID values must be tuned in advance. Other motor controllers with similar functions will work, we do not recommend any specific controller. Inputs

Pressure sensor – Receives a voltage proportional to the pressure in the patient’s lungs. Used to determine max pressure reached during inspiration, and to trigger when the patient is attempting to breathe in during assist mode. Minimum pressure sensor selection:

Differential (to sense negative pressures)
Range of up to 100 cm H2O. This is a 2x safety factor.
Accuracy on the order of 0.5 cm H2O

Note on Plumbing: The pressure sensor must be connected to the Ambu bag’s sensing port or somewhere in the airflow, as close as possible to the patient, past any valves.

Control knob potentiometers (POTs) should all be single turn, 10 KΩ. Single turn is to allow for specific settings to be marked on the face plate.

POT 1 – Varies inspired volume, sets angular oscillation of the arms. During operation, each arm varies by a maximum of approximately 20°, corresponding to fully squeezing a large bag. This dial varies position from 0% (fully open) to 100% (fully compressed).

POT 2 – Varies the BPM. This sets the rate from 0 to the maximum BPM given in the clinical document.

POT 3 – Varies the I:E ratio. Range as given in the clinical document.

Note: It is not essential that this be settable, one value greater than 1:1 can be selected and the POT repurposed as a threshold for over pressure. (Multiple clinicians have indicated that varying I:E is not critical.)

POT 4 – Sets the pressure threshold for detecting assist control. This varies as described in the clinical document.

Switch – Power on / off

E-stop – Instantly deactivates the system. This can be the main power switch, but a single pish must fully depower the system. This will allow the bag to be removed and immediate conversion to manual bagging in the case of any major failure.

Toggle Switch – Mode selection from volume to assist control.

Momentary Button 1 – Used to temporarily silence alarms. This must be debounced.

Momentary Button 1 – Used to confirm a change to one of the POTs. This is a necessary safety feature. This must be debounced.

Limit Switch – Used for homing the arms positions.
Output

LCD screen displays airway pressure in cm H2O. Other functions can be incorporated later. We are using a 20×4 character LCD display as this will display the minimum information, described in under interface. Any display better than this will be sufficient.

Audible alert buzzer will identify multiple fault conditions.

Electrical Hardware - MIT E-Vent | MIT Emergency Ventilator | https://e-vent.mit.edu/controls/electrical-hardware/
2 of 2 | 07/04/2020 19:59

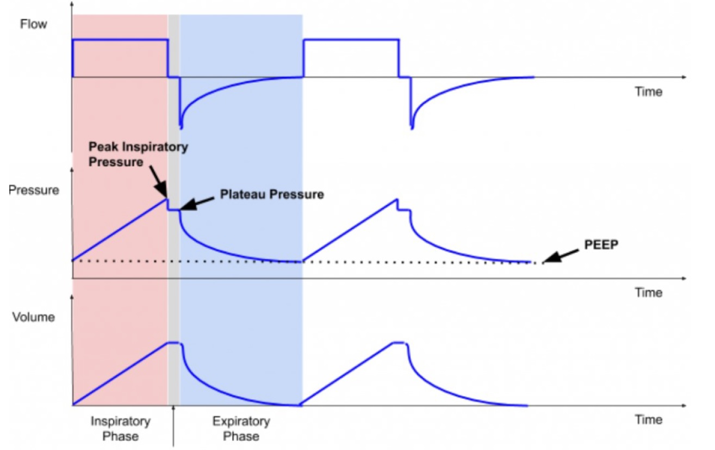
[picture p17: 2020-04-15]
EAR-Specs/MIT/MIT Curves.jpg

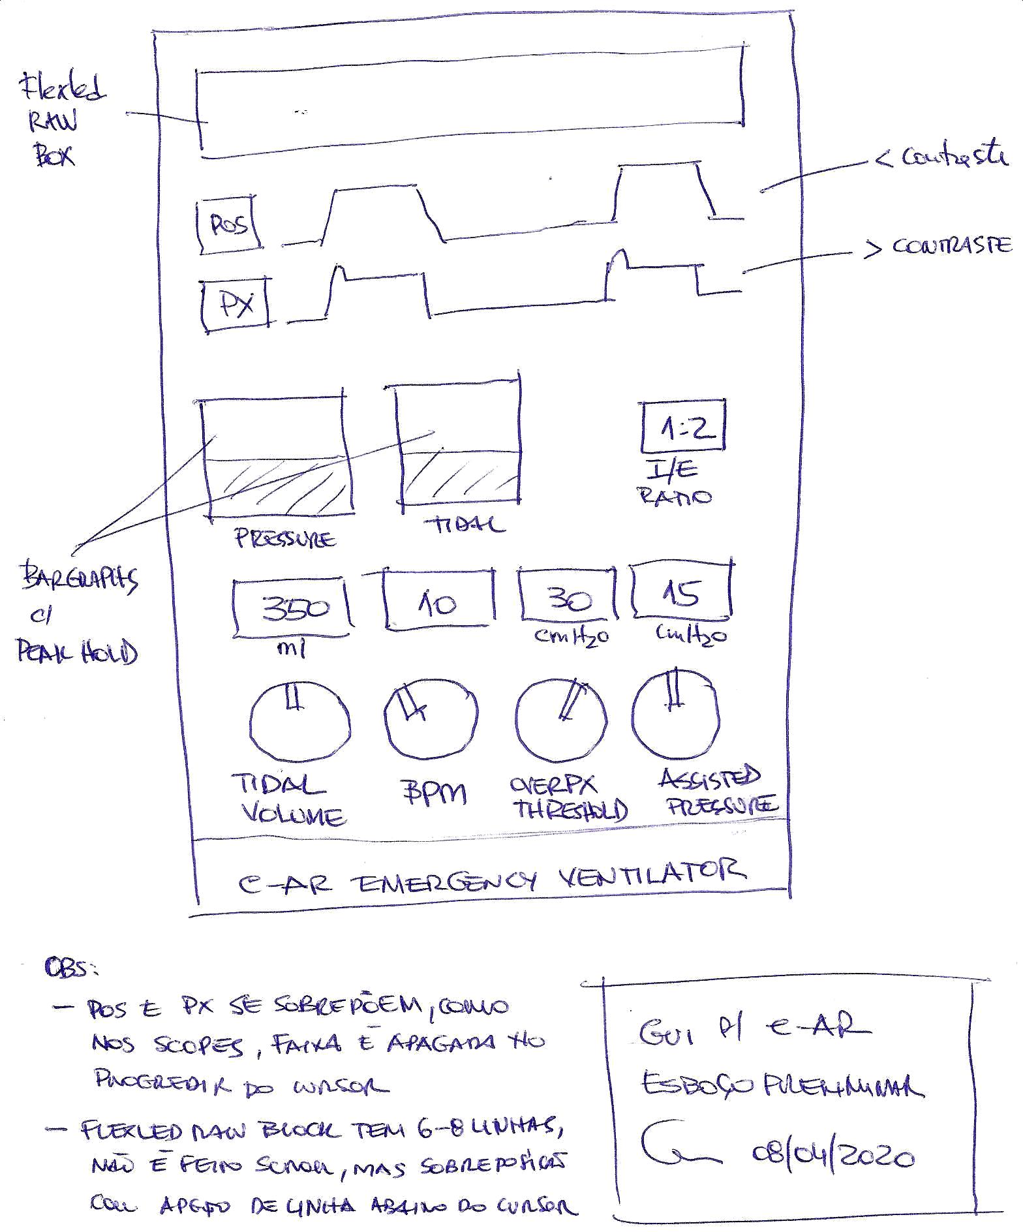
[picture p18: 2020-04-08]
PhotosAndVideos/200408 08.34 EAR GUI Sketch.jpg

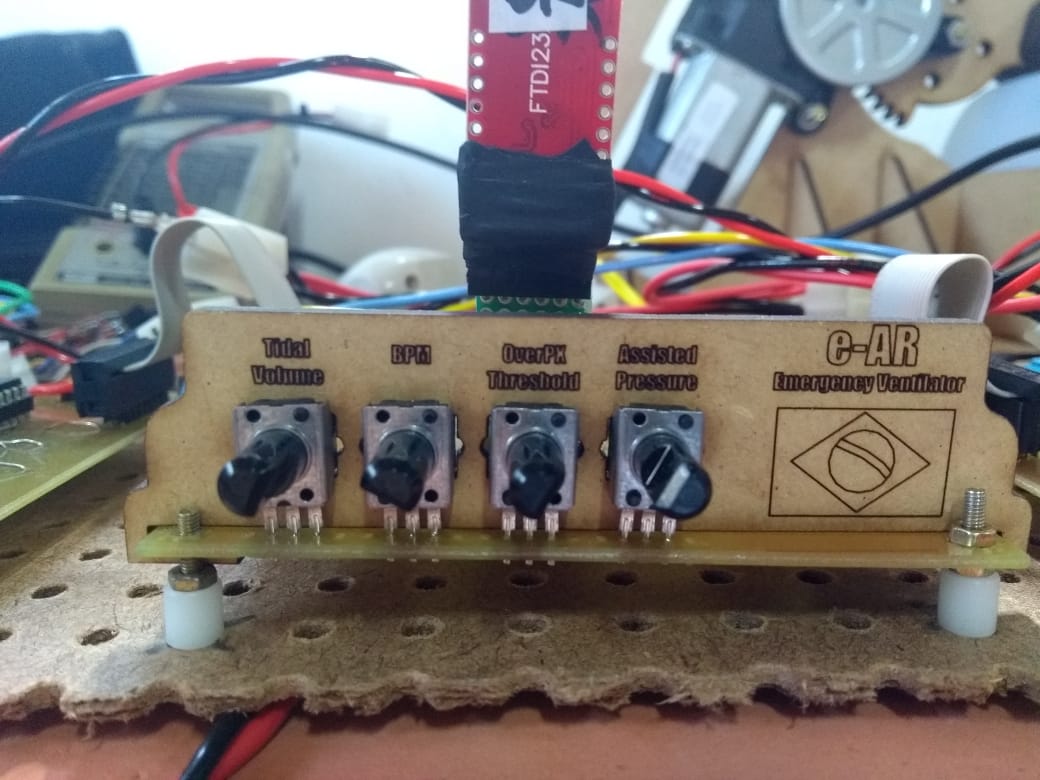
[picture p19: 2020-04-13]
PhotosAndVideos/200413 14.02 eAR Main Controls.jpeg

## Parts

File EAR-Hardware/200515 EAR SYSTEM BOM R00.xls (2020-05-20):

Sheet: Premissas
Premissas:
- Estimativas de custo FOB baseadas em custo para 1000 pcs na Digikey - historicamente são semelhantes aos preços landed na ADB (1997-2002)
- Itens nacionais estimados
Histórico de Revisões
- R01 em 13/08/2015 - incluidas posições de referência R1, R2,... C1,...
- R02 em 20/10/2015 - cabos passam a ser antichama 0,75mm2 (aprox 18AWG), estava expressa incorretamente em mm
- R03 em 19/04/2019
 | - Incluidas fases do processo: (S: Montagem SMT, P: Montagem PTH, I:Integração)
 | - Excluído conector phoenix
 | - Incluído placa FlexNet Cabeada

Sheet: PC2
 |  |  |  |  |  |  | Intern Costs Default (INT$): |  | Data Ref |  |  | INDEX |  | Data Ref |  | INDEX |  | Data Ref
 |  |  |  |  |  |  | USA: | 1.2 |  |  |  |  |  |  |  | Labor: | 1
 |  |  |  |  |  |  | China: |  |  |  |  | R$: | 1 |  |  | METAL: | 1
 |  |  |  |  |  |  | EU: |  |  |  |  | USD: | 5.5 |  |  | PLAST: | 1
 |  |  |  |  |  |  |  |  |  |  |  | EURO: | 6 |  |  | PCB: | 1
 |  |  | Cost Reference components (USD FOB para 1Kpcs)
 |  |  | TFR 1K 0603 1% | 0.0030
 |  |  | TFR 1K 0805 1% | 0.0050
 |  |  | TFR 1K 1206 1% | 0.0060
 |  |  | mlcc 0.1uF 50V X7R | 0.0120
 |  |  |  |  |  |  |  |  |  |  |  |  |  | No Taxes included (ICMS IPI)
Code |  | MFR P/N | Component description | QTY | REF POS | Fase | UC$FOB | INT $ | UC$CIF | IX $ | CK CUP$ | CUP R$ | IX R$ | CK CT R$ | Import Content | Local Content | %Total | %Import | OBS
PRD001 |  |  | PC2 | 1 |  |  |  |  |  |  |  |  |  | 387.92 | 292.92 | 95.00 | 100.00% | 75.51%
APCB00001 | F |  | APCB00001 - Assembled PCB eAR ECU | 1 |  |  |  |  |  |  |  |  |  | 82.03 | 82.03 | 0.00 | 21.15% | 100.00%
APCB00002 | F |  | APCB00002 - Assembled PCB Px Sensor | 1 |  |  |  |  |  |  |  |  |  | 51.17 | 51.17 | 0.00 | 13.19% | 100.00%
LABPCM00001 |  |  | PCM00001 assembly** cost | 1 |  |  | 0.0000 | 1.2 | 0.0000 | 5.5 | 0.0000 | 35.0000 | 1 | 35.0000 | 0.0000 | 35.0000 | 9.02% | 0.00%
LABPCM00002 |  |  | PCM00002 assembly** cost | 1 |  |  | 0.0000 | 1.2 | 0.0000 | 5.5 | 0.0000 | 10.0000 | 1 | 10.0000 | 0.0000 | 10.0000 | 2.58% | 0.00%
 |  |  | eAR metallic Housing | 1 |  |  | 0.0000 | 1.2 | 0.0000 | 5.5 | 0.0000 | 20.0000 | 1 | 20.0000 | 0.0000 | 20.0000 | 5.16% | 0.00%
 |  | Mabuchi | eAR Arm Motor | 1 |  |  | 7.0000 | 1.2 | 8.4000 | 5.5 | 46.2000 |  | 1 | 46.2000 | 46.2000 | 0.0000 | 11.91% | 100.00%
 |  |  | eAR Mech stucture Kit (arm, motor skeleton) | 1 |  |  | 0.0000 | 1.2 | 0.0000 | 5.5 | 0.0000 | 15.0000 | 1 | 15.0000 | 0.0000 | 15.0000 | 3.87% | 0.00%
 |  |  | eAR female MiniFit 16 way connector with preset cables | 1 |  |  | 1.0000 | 1.2 | 1.2000 | 5.5 | 6.6000 |  | 1 | 6.6000 | 6.6000 | 0.0000 | 1.70% | 100.00%
 |  |  | eAR Harness Kit | 1 |  |  | 3.0000 | 1.2 | 3.6000 | 5.5 | 19.8000 |  | 1 | 19.8000 | 19.8000 | 0.0000 | 5.10% | 100.00%
 |  |  | eAR Arm Position Sensor | 1 |  |  | 5.0000 | 1.2 | 6.0000 | 5.5 | 33.0000 |  | 1 | 33.0000 | 33.0000 | 0.0000 | 8.51% | 100.00%
 |  |  | AMBU removable shelf | 1 |  |  | 0.0000 | 1.2 | 0.0000 | 5.5 | 0.0000 | 15.0000 | 1 | 15.0000 | 0.0000 | 15.0000 | 3.87% | 0.00%
 |  |  | AMBU In/Out fast connectors | 2 |  |  | 2.0000 | 1.2 | 2.4000 | 5.5 | 13.2000 |  | 1 | 26.4000 | 26.4000 | 0.0000 | 6.81% | 100.00%
 |  |  | eAR mech kit (screws, bolts, washer, spacers) | 1 |  |  | 1.0000 | 1.2 | 1.2000 | 5.5 | 6.6000 |  | 1 | 6.6000 | 6.6000 | 0.0000 | 1.70% | 100.00%
 |  |  | Px Sns Cable - MiniFit4 w/ 3 cables BLK1/BLU3/YEL4 2m long | 1 |  |  | 2.0000 | 1.2 | 2.4000 | 5.5 | 13.2000 |  | 1 | 13.2000 | 13.2000 | 0.0000 | 3.40% | 100.00%
 |  |  | eAR Px Sensor plastic Housing | 1 |  |  | 1.0000 | 1.2 | 1.2000 | 5.5 | 6.6000 |  | 1 | 6.6000 | 6.6000 | 0.0000 | 1.70% | 100.00%
 |  |  | eAR Px Sensor tube | 1 |  |  | 0.2000 | 1.2 | 0.2400 | 5.5 | 1.3200 |  | 1 | 1.3200 | 1.3200 | 0.0000 | 0.34% | 100.00%
 |  |  | assembly** means all production phases: SMT/PTH/PRGM/Test
 |  |  | Sub-assembly eAR ECU PCB
APCB00001 |  |  | APCB Assembly eAR ECU option ATMega328 on PCB | 1 |  |  |  |  |  |  |  |  |  | 82.0314 | 82.0314 | 0.0000 | 21.15% | 100.00%
 |  |  | PCB FR4 eAR ECU 10x10cm | 1 | PCI |  | 1.5000 | 1.2 | 1.8000 | 5.5 | 9.9000 |  | 1 | 9.9000 | 9.9000 | 0.0000 | 2.55% | 100.00%
 |  |  |  | 1 |  |  | 0.0720 | 1.2 | 0.0864 | 5.5 | 0.4752 |  | 1 | 0.4752 | 0.4752 | 0.0000 | 0.12% | 100.00%
 |  |  |  | 1 |  |  | 0.2400 | 1.2 | 0.2880 | 5.5 | 1.5840 |  | 1 | 1.5840 | 1.5840 | 0.0000 | 0.41% | 100.00%
 |  |  |  | 1 |  |  | 0.0050 | 1.2 | 0.0060 | 5.5 | 0.0330 |  | 1 | 0.0330 | 0.0330 | 0.0000 | 0.01% | 100.00%
 |  |  | Potentiometer plastic plate | 1 |  |  | 0.0100 | 1.2 | 0.0120 | 5.5 | 0.0660 |  | 1 | 0.0660 | 0.0660 | 0.0000 | 0.02% | 100.00%
 |  |  | Potentiometer Knob | 4 |  |  | 0.1000 | 1.2 | 0.1200 | 5.5 | 0.6600 |  | 1 | 2.6400 | 2.6400 | 0.0000 | 0.68% | 100.00%
 |  |  | Screw Terminal 01x02 5mm pitch | 3 | ARM_SENSE1, Motor1, PSU1 |  | 0.2500 | 1.2 | 0.3000 | 5.5 | 1.6500 |  | 1 | 4.9500 | 4.9500 | 0.0000 | 1.28% | 100.00%
 |  |  | Conn_01x02 | 1 | ASSIST1 |  | 0.0500 | 1.2 | 0.0600 | 5.5 | 0.3300 |  | 1 | 0.3300 | 0.3300 | 0.0000 | 0.09% | 100.00%
 |  |  | Buzzer 12mm 5 or 7mm pitch | 1 | BZ1 |  | 0.2000 | 1.2 | 0.2400 | 5.5 | 1.3200 |  | 1 | 1.3200 | 1.3200 | 0.0000 | 0.34% | 100.00%
 |  |  | Alum Electrolytic Cap 470uF/35V | 1 | C1 |  | 0.1500 | 1.2 | 0.1800 | 5.5 | 0.9900 |  | 1 | 0.9900 | 0.9900 | 0.0000 | 0.26% | 100.00%
 |  |  | MLCC 100nF X7R 50V | 16 | C2, C4, C5, C6, C7, C8, C9, C10, C11, C13, C14, C18, C19, C21, C24, C25 |  | 0.0120 | 1.2 | 0.0144 | 5.5 | 0.0792 |  | 1 | 1.2672 | 1.2672 | 0.0000 | 0.33% | 100.00%
 |  |  | Alum Electrolytic Cap 47uF/50V | 5 | C3, C12, C15, C16, C17 |  | 0.0500 | 1.2 | 0.0600 | 5.5 | 0.3300 |  | 1 | 1.6500 | 1.6500 | 0.0000 | 0.43% | 100.00%
 |  |  | MLCC 10uF 0805 X5R 10V | 1 | C20 |  | 0.0500 | 1.2 | 0.0600 | 5.5 | 0.3300 |  | 1 | 0.3300 | 0.3300 | 0.0000 | 0.09% | 100.00%
 |  |  | cer cap 22pF NP0 | 2 | C22, C23 |  | 0.0100 | 1.2 | 0.0120 | 5.5 | 0.0660 |  | 1 | 0.1320 | 0.1320 | 0.0000 | 0.03% | 100.00%
 |  |  | S3G SMC | 1 | D1 |  | 0.1000 | 1.2 | 0.1200 | 5.5 | 0.6600 |  | 1 | 0.6600 | 0.6600 | 0.0000 | 0.17% | 100.00%
 |  |  | S1J SOD123 | 5 | D2, D3, D4, D5, D6 |  | 0.0200 | 1.2 | 0.0240 | 5.5 | 0.1320 |  | 1 | 0.6600 | 0.6600 | 0.0000 | 0.17% | 100.00%
 |  |  | Molex Mini-Fit Jr 2x8PIN RA PCB Header | 1 | EXP1 |  | 0.2500 | 1.2 | 0.3000 | 5.5 | 1.6500 |  | 1 | 1.6500 | 1.6500 | 0.0000 | 0.43% | 100.00%
 |  |  | PinHeader_02x03_RA | 1e-09 | EXT_INT1, EXT_INT2 |  | 0.0001 | 1.2 | 0.0001 | 5.5 | 0.0007 |  | 1 | 6.6e-13 | 6.6e-13 | 0.0000 | 1.701376465e-13% | 100.00%
 |  |  | 2,5A PPTC | 1 | F1 |  | 0.0500 | 1.2 | 0.0600 | 5.5 | 0.3300 |  | 1 | 0.3300 | 0.3300 | 0.0000 | 0.09% | 100.00%
 |  |  | Conn_01x02 | 1e-09 | FDC1, FDC2 |  | 0.0001 | 1.2 | 0.0001 | 5.5 | 0.0007 |  | 1 | 6.6e-13 | 6.6e-13 | 0.0000 | 1.701376465e-13% | 100.00%
 |  |  | MountingHole PCB Plastic Spacer TBD | 4 | H1, H2, H3, H4 |  | 0.0300 | 1.2 | 0.0360 | 5.5 | 0.1980 |  | 1 | 0.7920 | 0.7920 | 0.0000 | 0.20% | 100.00%
 |  |  | Female Header_02x03 | 1 | JP1 |  | 0.1000 | 1.2 | 0.1200 | 5.5 | 0.6600 |  | 1 | 0.6600 | 0.6600 | 0.0000 | 0.17% | 100.00%
 |  |  | Hi_VD_3mm R/A | 1 | LD1 |  | 0.2000 | 1.2 | 0.2400 | 5.5 | 1.3200 |  | 1 | 1.3200 | 1.3200 | 0.0000 | 0.34% | 100.00%
 |  |  | Hi_VD_0805 | 1e-09 | LD2 |  | 0.0001 | 1.2 | 0.0001 | 5.5 | 0.0007 |  | 1 | 6.6e-13 | 6.6e-13 | 0.0000 | 1.701376465e-13% | 100.00%
 |  |  | Hi_VM_3mm R/A | 1 | LD3 |  | 0.2000 | 1.2 | 0.2400 | 5.5 | 1.3200 |  | 1 | 1.3200 | 1.3200 | 0.0000 | 0.34% | 100.00%
 |  |  | Hi_VM_0805 | 1e-09 | LD4 |  | 0.0001 | 1.2 | 0.0001 | 5.5 | 0.0007 |  | 1 | 6.6e-13 | 6.6e-13 | 0.0000 | 1.701376465e-13% | 100.00%
 |  |  | PinHeader_01x12 | 1e-09 | P1, P5 |  | 0.0001 | 1.2 | 0.0001 | 5.5 | 0.0007 |  | 1 | 6.6e-13 | 6.6e-13 | 0.0000 | 1.701376465e-13% | 100.00%
 |  |  | PinHeader_01x02 | 1e-09 | P2, P6 |  | 0.0001 | 1.2 | 0.0001 | 5.5 | 0.0007 |  | 1 | 6.6e-13 | 6.6e-13 | 0.0000 | 1.701376465e-13% | 100.00%
 |  |  | PinHeader_01x06 | 1 | P3 |  | 0.1000 | 1.2 | 0.1200 | 5.5 | 0.6600 |  | 1 | 0.6600 | 0.6600 | 0.0000 | 0.17% | 100.00%
 |  |  | PinHeader_01x05 | 1e-09 | P4 |  | 0.0001 | 1.2 | 0.0001 | 5.5 | 0.0007 |  | 1 | 6.6e-13 | 6.6e-13 | 0.0000 | 1.701376465e-13% | 100.00%
 |  |  | Molex Mini-Fit Jr 2x2PIN RA PCB Header | 1 | PX1 |  | 0.1500 | 1.2 | 0.1800 | 5.5 | 0.9900 |  | 1 | 0.9900 | 0.9900 | 0.0000 | 0.26% | 100.00%
 |  |  | BC817 NPN GP 40V 100mA SOT23 | 3 | Q1, Q3, Q12 |  | 0.0200 | 1.2 | 0.0240 | 5.5 | 0.1320 |  | 1 | 0.3960 | 0.3960 | 0.0000 | 0.10% | 100.00%
 |  |  | MMBTA06 NPN GP 80V 100mA SOT23 | 4 | Q2, Q4, Q10, Q13 |  | 0.0300 | 1.2 | 0.0360 | 5.5 | 0.1980 |  | 1 | 0.7920 | 0.7920 | 0.0000 | 0.20% | 100.00%
 |  |  | MMBTA56 PNP GP 80V 100mA SOT23 | 2 | Q5, Q11 |  | 0.0300 | 1.2 | 0.0360 | 5.5 | 0.1980 |  | 1 | 0.3960 | 0.3960 | 0.0000 | 0.10% | 100.00%
 |  |  | IRLR3410PbF N-CH 60V LL Drive Current>10A | 4 | Q6, Q7, Q8, Q9 |  | 0.3000 | 1.2 | 0.3600 | 5.5 | 1.9800 |  | 1 | 7.9200 | 7.9200 | 0.0000 | 2.04% | 100.00%
 |  |  | TFR 0805 5% 1M | 4 | R1, R2, R3, R4 |  | 0.0050 | 1.2 | 0.0060 | 5.5 | 0.0330 |  | 1 | 0.1320 | 0.1320 | 0.0000 | 0.03% | 100.00%
 |  |  | TFR 0805 5% 100R | 17 | R5, R6, R7, R8, R9, R10, R11, R12, R13, R14, R19, R26, R29, R30, R32, R38, R49 |  | 0.0050 | 1.2 | 0.0060 | 5.5 | 0.0330 |  | 1 | 0.5610 | 0.5610 | 0.0000 | 0.14% | 100.00%
 |  |  | TFR 0805 5% 10K | 26 | R15, R16, R18, R21, R24, R25, R34, R37, R39, R45, R51, R52, R53, R54, R55, R56, R57, R58, R59, R60, R61, R62, R63, R64, R65, R66 |  | 0.0050 | 1.2 | 0.0060 | 5.5 | 0.0330 |  | 1 | 0.8580 | 0.8580 | 0.0000 | 0.22% | 100.00%
 |  |  | TFR 0805 5% 1K | 7 | R17, R20, R27, R31, R35, R36, R40 |  | 0.0050 | 1.2 | 0.0060 | 5.5 | 0.0330 |  | 1 | 0.2310 | 0.2310 | 0.0000 | 0.06% | 100.00%
 |  |  | TFR 0805 5% 33K | 1 | R22 |  | 0.0050 | 1.2 | 0.0060 | 5.5 | 0.0330 |  | 1 | 0.0330 | 0.0330 | 0.0000 | 0.01% | 100.00%
 |  |  | TFR 0805 5% 100K | 11 | R23, R28, R33, R41, R42, R43, R44, R46, R47, R48, R50 |  | 0.0050 | 1.2 | 0.0060 | 5.5 | 0.0330 |  | 1 | 0.3630 | 0.3630 | 0.0000 | 0.09% | 100.00%
 |  |  | B10K Linear potentiometer 10K PTH pitch 200mils | 4 | R_POT1, R_POT2, R_POT3, R_POT4 |  | 0.5000 | 1.2 | 0.6000 | 5.5 | 3.3000 |  | 1 | 13.2000 | 13.2000 | 0.0000 | 3.40% | 100.00%
 |  |  | 0R1 PTH 5W 5% | 1e-09 | RS1 |  | 0.0001 | 1.2 | 0.0001 | 5.5 | 0.0007 |  | 1 | 6.6e-13 | 6.6e-13 | 0.0000 | 1.701376465e-13% | 100.00%
 |  |  | 2512 0R1 2W 5% | 1 | RS2 |  | 0.1000 | 1.2 | 0.1200 | 5.5 | 0.6600 |  | 1 | 0.6600 | 0.6600 | 0.0000 | 0.17% | 100.00%
 |  |  | AVR-ISP-6 | 1 | SPI1 |  | 0.0500 | 1.2 | 0.0600 | 5.5 | 0.3300 |  | 1 | 0.3300 | 0.3300 | 0.0000 | 0.09% | 100.00%
 |  |  | PinHeader_02x08 | 1 | SPI_BASED_SLOW_IO1 |  | 0.1000 | 1.2 | 0.1200 | 5.5 | 0.6600 |  | 1 | 0.6600 | 0.6600 | 0.0000 | 0.17% | 100.00%
 |  |  | L7805 | 1 | U1 |  | 0.1000 | 1.2 | 0.1200 | 5.5 | 0.6600 |  | 1 | 0.6600 | 0.6600 | 0.0000 | 0.17% | 100.00%
 |  |  | LM358D soic narrow | 1 | U2 |  | 0.1500 | 1.2 | 0.1800 | 5.5 | 0.9900 |  | 1 | 0.9900 | 0.9900 | 0.0000 | 0.26% | 100.00%
 |  |  | LM393D soic narrow | 1 | U3 |  | 0.1500 | 1.2 | 0.1800 | 5.5 | 0.9900 |  | 1 | 0.9900 | 0.9900 | 0.0000 | 0.26% | 100.00%
 |  |  | ATmega328-AU | 1 | U4 |  | 1.7000 | 1.2 | 2.0400 | 5.5 | 11.2200 |  | 1 | 11.2200 | 11.2200 | 0.0000 | 2.89% | 100.00%
 |  |  | 74HC595D soic narrow | 1 | U5 |  | 0.1500 | 1.2 | 0.1800 | 5.5 | 0.9900 |  | 1 | 0.9900 | 0.9900 | 0.0000 | 0.26% | 100.00%
 |  |  | 74HC165D soic narrow | 1 | U6 |  | 0.1500 | 1.2 | 0.1800 | 5.5 | 0.9900 |  | 1 | 0.9900 | 0.9900 | 0.0000 | 0.26% | 100.00%
 |  |  | ULN2803ADW soic wide | 1 | U7 |  | 0.4500 | 1.2 | 0.5400 | 5.5 | 2.9700 |  | 1 | 2.9700 | 2.9700 | 0.0000 | 0.77% | 100.00%
 |  |  | ULN2803AP | 1e-09 | U8 |  | 0.0001 | 1.2 | 0.0001 | 5.5 | 0.0007 |  | 1 | 6.6e-13 | 6.6e-13 | 0.0000 | 1.701376465e-13% | 100.00%
 |  |  | S14K14 Varistor 14VAC 14mm | 1 | V1 |  | 0.1500 | 1.2 | 0.1800 | 5.5 | 0.9900 |  | 1 | 0.9900 | 0.9900 | 0.0000 | 0.26% | 100.00%
 |  |  | PinHeader 02x03 | 1 | WDT1 |  | 0.0500 | 1.2 | 0.0600 | 5.5 | 0.3300 |  | 1 | 0.3300 | 0.3300 | 0.0000 | 0.09% | 100.00%
 |  |  | xtal 16MHz HC49 low profile | 1 | X1 |  | 0.1000 | 1.2 | 0.1200 | 5.5 | 0.6600 |  | 1 | 0.6600 | 0.6600 | 0.0000 | 0.17% | 100.00%
 |  |  | Sub-assembly Px Sensor
APCB00002 |  |  | APCB Assembly Px Sensor | 1 |  |  |  |  |  |  |  |  |  | 51.1698 | 51.1698 | 0.0000 | 13.19% | 100.00%
 |  |  | PCB FR4 eAR Px Sensor | 1 | PCI |  | 0.4000 | 1.2 | 0.4800 | 5.5 | 2.6400 |  | 1 | 2.6400 | 2.6400 | 0.0000 | 0.68% | 100.00%
 |  |  | MLCC 100nF X7R 50V | 2 | C1, C2 |  | 0.0120 | 1.2 | 0.0144 | 5.5 | 0.0792 |  | 1 | 0.1584 | 0.1584 | 0.0000 | 0.04% | 100.00%
 |  |  | Molex Mini-Fit Jr 2x2PIN RA PCB Header | 1 | PX1 |  | 0.1500 | 1.2 | 0.1800 | 5.5 | 0.9900 |  | 1 | 0.9900 | 0.9900 | 0.0000 | 0.26% | 100.00%
 |  |  | TFR 0805 5% 0R | 1 | R2B1 |  | 0.0050 | 1.2 | 0.0060 | 5.5 | 0.0330 |  | 1 | 0.0330 | 0.0330 | 0.0000 | 0.01% | 100.00%
 |  |  | TFR 0805 5% 47K | 17 | R1B1 |  | 0.0050 | 1.2 | 0.0060 | 5.5 | 0.0330 |  | 1 | 0.5610 | 0.5610 | 0.0000 | 0.14% | 100.00%
 |  | NXP MPX5010DP | Pressure Sensor 100 Kpa | 1 | PX1 |  | 7.0000 | 1.2 | 8.4000 | 5.5 | 46.2000 |  | 1 | 46.2000 | 46.2000 | 0.0000 | 11.91% | 100.00%
 |  |  | Female PinHeader_01x06 | 1 | PX1 |  | 0.0500 | 1.2 | 0.0600 | 5.5 | 0.3300 |  | 1 | 0.3300 | 0.3300 | 0.0000 | 0.09% | 100.00%
 |  |  | M3 Screw 20mm conic head | 1 |  |  | 0.0050 | 1.2 | 0.0060 | 5.5 | 0.0330 |  | 1 | 0.0330 | 0.0330 | 0.0000 | 0.01% | 100.00%
 |  |  | M3 Bolt | 6 |  |  | 0.0050 | 1.2 | 0.0060 | 5.5 | 0.0330 |  | 1 | 0.1980 | 0.1980 | 0.0000 | 0.05% | 100.00%
 |  |  | M3 washer | 2 |  |  | 0.0020 | 1.2 | 0.0024 | 5.5 | 0.0132 |  | 1 | 0.0264 | 0.0264 | 0.0000 | 0.01% | 100.00%

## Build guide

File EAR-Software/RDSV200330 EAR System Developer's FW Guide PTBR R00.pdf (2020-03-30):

Doc.: RDSV200330 EAR System Developer's FW Guide PTBR R00 | 1/7

_____________________________________________________________________________

| Data | Signatures
Author: | 30/03/2020 | | Títle: Guia do Desenvolvedor Sistema EAR - FW
Verif.:

Aprov.:

### 1. Escopo

O objetivo deste documento é descrever os aspectos necessários do sistema EAR para possibilitar o desenvolvimento do “firmware” da ECU EAR. É indispensável a leitura prévia da última versão do documento “EAR System Developer's HW Guide” para que o desenvolvedor de software entenda o sistema EAR e seu HW.

Estão previstas ampliações de escopo do projeto para suportar respiração assistida, Somente para os pacientes em fase de recuperação. A eletrônica do projeto EAR já contempla expansões para esta função e outras.

Este projeto pode ser alterado a qualquer momento, sem aviso prévio.

Disclaimer: não assumimos nenhuma responsabilidade sobre qualquer dispositivo construído a partir das informações deste documento e orientamos para que os dispositivos sejam projetados na estrita observância às normas locais, que sigam as recomendações de especialistas e que sejam homologados pelas agências reguladoras em todas as fases.

### 2. Controle do Documento

- 30/03/2020: Emissão R00 – Português BR
- definidos requisitos gerais
- definidos em FW01: testes de hardware e ferramentas necessárias para próximas etapas
- definidos em FW01: testes para podermos modelar parâmetros importantes de funcionamento
- operação com paciente a ser implementada

### 3. Referências

- Open Source COVID19 Medical Supplies facebook: https://www.facebook.com/groups/670932227050506/
- COVID-19 Air BRASIL - Fast production of assisted ventilation devices https://www.facebook.com/groups/235476464265909/
- RDSV200320 Emergency Automatic Respirator Specification R00 – Preliminary
- RDSV200322 EAR Hardware Proposition Draft R00 – PTBR
- MIT E-Vent – “Key Ventilation Specifications”
- RDSV200329 EAR System Developer's HW Guide PTBR R00

Doc.: RDSV200330 EAR System Developer's FW Guide PTBR R00 | 2/7

### 4. Abreviaturas utilizadas

Abreviaturas e termos utilizadas em todo o documento:
- EAR: Emergency Automotic Respirator
- FDC: Fim de Curso
- BAG: bolsa de ar, pode ser a do AMBU ou a do FIO2
- AMBU: Equipamento médico existente, utilizamos somente o BAG para comprimir ar para o paciente
- FIO2: Fraction of Inspired O2 define a proporção de O2 no ar inspirado pelo paciente
- ECU: Electronic Control Unit
- PEEP: Pressão positiva expiratória final. Para eletrônicos e SW developers, se trata de um “Offset DC” na pressão do ar do pulmão do paciente. A pressão nunca cai a menos de 5-10cm de H20.
- HEPA: tecnologia empregada em filtros de ar com alta eficiência na separação de partículas (wikipedia)
- NPN: polaridade da conexão do sensor ou atuador, comuta ou é comutado pelo GND (Low Side)
- SPI: Serial Peripheral Interface, interface serial síncrona, baseada em registradores de deslocamento
- WIP: Work in Progress, trabalho não finalizado
- GPIO: General Purpose IO, ou porta de uso geral do arduíno
- SOA: Safe operating area, ou área de operação segura do componente
- Pots: Potenciômetros
- CW: Clockwise ou sentido de compressão do AMBU (A+ B-)
- CCW: Counterclockwise ou descompressão do AMBU (A- B+)

### 5. Considerações Iniciais, Requisitos Básicos, Visão Global do Sistema EAR, Visão Geral

do Hardware Controlado pelo Sistema EAR

Ver RDSV200329 EAR System Developer's HW Guide PTBR R00.

### 6. Requisitos do SW ECU EAR

### 6.1. Requisitos Gerais

### 6.1.1. Target HW

Qualquer firmware deve ser desenvolvido para rodar em um Arduíno Pro Mini, mediante bootloader. Embora tenha sido previsto um conector ICSP no hardware, não disponível no Arduíno Pro Mini, isto exigiria um equipamento de gravação AVR que pode não ser disponível.

- Pinout do Arduino Pro Mini:
PINO | FUNÇÃO PINO | OBSERVAÇÕES
TXO | TXO | Tx Bootloader, monitor serial ou TxD Rede
RXI | RXI | Rx Bootloader, monitor serial ou RxD Rede
RST | /RESET | Reset geral, para acionamento usar open collector NPN

Doc.: RDSV200330 EAR System Developer's FW Guide PTBR R00 | 3/7
GND | GND | GND
D2 | GPIO | Reservado Rede_RTS
D3 | GPIO | Latch Inputs expansor de IO – SH /LD 74HC165
D4 | GPIO | Buzzer OUT
D5 | GPIO | Motor Low Side B
D6 | PWM | PWM Motor Hi Side B
D7 | GPIO | Checklamp LED Vermelho
D8 | GPIO | Motor Low Side A
D9 | PWM | PWM Motor Hi Side A
D10 | GPIO | Latch Outputs expansor de IO – RCK 74HC595 +Edge
D11 | MOSI | MOSI expansor de IO
D12 | MISO | MISO expansor de IO
D13 | SCK | SCK expansor de IO – normalmente ligado a um LED
A0 | AN0 | Leitura Analógica POT1
A1 | AN1 | Leitura Analógica POT2
A2 | AN2 | Leitura Analógica POT3
A3 | AN3 | Leitura Analógica POT4 ou futura entrada Multiplex AN
VCC | VCC | +5V
RST | /RESET | Reset geral, para acionamento usar open collector NPN
GND | GND | GND
RAW | RAW | Não Conectado – Recomendado remover o regulador interno do Arduíno.
A7 | AN7 | Leitura Analógica Corrente do Motor
A6 | AN6 | Leitura Analógica Elemento Externo (ex: Sensor Pressão)
A5 | AN5 | Leitura V_Motor após PPTC
A4 | AN4 | Reservado

### 6.1.2. Dump Serial

IMPORTANTE: Todo software desenvolvido deve dumpar, via monitor serial, em Ascii e e em tempo real, os dados relevantes do sistema, tais como:

- Posições lidas dos pots
- Fase do processo respiratório
- Warnings e Erros
- Estados de máquinas de estado importantes (ME do Motor, etc)

Na inicialização devem ser reportados Tipo de FW, Versão de FW, Parms em memória não volátil, Erros, se puderem ser recuperados da RAM, ou Erros graves armazenados em NVM.

Sugerimos que esta seja a primeira coisa a ser implementada, para termos uma ferramenta de auxílio ao desenvolvimento do firmware. A taxa de transmissão deve ser a mesma utilizada para o bootloader, 57K6 bps. Esta ferramenta será doravante denominada FlexLed.

Doc.: RDSV200330 EAR System Developer's FW Guide PTBR R00 | 4/7

### 6.1.3. Tratamento de IO baseado em SPI

- o Projeto EAR tem expansão de IOs lentos, via SPI, por módulos. Cada módulo proporciona 8 entradas para sensores NPN e 8 saídas para relés com acionamento NPN. Denominamos lentos porque não serão frequentemente lidos ou atualizados, as taxas vão depender da implementação de software específica, mas penso que devem ficar no range de 1 a 10 ms entre cada atualização. Um dos gargalos importantes é a leitura dos sensores que promovem o desligamento dos motores, quanto maior o tempo entre leituras, mais o motor irá se deslocar. Cuidado deve ser tomado para ter bufferização de todas estas saídas em software, porque as leituras das entradas sobreescrevem, SEMPRE, as saídas. Embora as saídas necessitem de um sinal de “Latch_Outputs” para serem efetivadas, um pequeno ruído elétrico pode promover isto.

O tratamento de IO baseado em SPI é bastante simples, mas alguns cuidados devem ser tomados: antes de realizar as transações devemos realizar um pulso negativo em Latch_Inputs (D3) para carregar as leituras nos registradores de deslocamento do 74HC165 a serem lidos pela SPI e após as transações devemos realizar uma pulso positivo em Latch_Outputs para validar os dados transmitidos via SPI para o 74HC595.

É importante entender a CPI

- ver https://www.arduino.cc/en/reference/SPI e exemplos
- tratar a SPI em módulos de 8 bits
- lembrar que o número de entradas e saídas podem variar, sempre em módulos de 8. Assim podemos ter 8, 16, 24 ou 32 saídas e entradas. Todas as saídas tem que ser bufferizadas em software, porque as leituras das entradas sobreescrevem, SEMPRE, as saídas. Embora as saídas necessitem de um sinal de “Latch_Outputs” para serem efetivadas, um pequeno ruído elétrico pode provocar isto.

Exemplo, podemos ter um vetor InputsExp [4] e OutputsExp [4]. O procedimento vai ser dependente do número de placas que tivermos.

#include <SPI.h>

byte InputsExp [4];
byte OutputsExp [4];
#define Latch_Inputs

#define Latch_Outputs 10 // deve ser inicializada com 0

#define Latch_Inputs 3

// antes do procedimento SPI utilizar
digitalWrite(Latch_Inputs, LOW); // garante que houve a transferência, realizada por nível, do HC165
// talvez precise inserir aqui um pequeno delay de alguns microssegundos digitalWrite(Latch_Inputs, HIGH); // habilita operação HC165 como shift register
// depois do procedimento SPI utilizar
digitalWrite(Latch_Outputs, HIGH);

Doc.: RDSV200330 EAR System Developer's FW Guide PTBR R00 | 5/7

// talvez precise inserir aqui um pequeno delay de alguns microssegundos digitalWrite(Latch_Outputs, LOW);

procedimento para 1 placa:
SPI.beginTransaction();
InputsExp[0]=SPI.transfer(OutputsExp[0]); SPI.endTransaction();

procedimento para 2 placas: SPI.beginTransaction();
InputsExp[0]=SPI.transfer(OutputsExp[1]); InputsExp[1]=SPI.transfer(OutputsExp[0]); SPI.endTransaction();

procedimento para 3 placas: SPI.beginTransaction();
InputsExp[0]=SPI.transfer(OutputsExp[2]); InputsExp[1]=SPI.transfer(OutputsExp[1]); InputsExp[2]=SPI.transfer(OutputsExp[0]); SPI.endTransaction();

procedimento para 4 placas: SPI.beginTransaction();
InputsExp[0]=SPI.transfer(OutputsExp[3]); InputsExp[1]=SPI.transfer(OutputsExp[2]); InputsExp[2]=SPI.transfer(OutputsExp[1]); InputsExp[3]=SPI.transfer(OutputsExp[0]); SPI.endTransaction();

### 6.2. Requisitos para o FW01 - Teste de Hardware

O objetivo do FW01 é possibilitar um teste simples para verificar se o hardware da EAR ECU é funcional.
Devem ser verificados:
- funcionamento e excursão dos pots (verificação via FlexLed está OK)
- funcionamento dos módulos de expansão de IO, mediante testes com loopback** de entradas e saídas. **loopback significa: IN1A ligado a OUT1-1, IN1B ligado a OUT11-2 e assim por diante. Lembrar que se foi montado um ULN2003 não haverá um pino de saída em OUT1-1 e o software deve reportar a falha.
- funcionamento do driver de motor, de acordo com o tipo de driver montado: relé ou mosfet.

### 6.2.1. Testes dos Pots

- basta realizar a leitura dos pots e reportar no FlexLed algo do tipo P1xx P2yy P3zz e P4ww onde xx, yy, zz e ww podem ser as leituras analógicas dos pots dos 8 bits mais significativos do ADC, representadas em hexadecimal.

Doc.: RDSV200330 EAR System Developer's FW Guide PTBR R00 | 6/7

### 6.2.2. Funcionamento dos módulos de expansão de IO

- basta realizar escritas e leituras dos IOs baseados em SPI e reportar no FlexLed o resultado.
Uma sequência de testes exemplo nesta primeira fase poderia ser algo do tipo:

Tx00000001 Rx00000001
Tx00000010 Rx00000010
Tx10000000 Rx10000000

Os resultados podem ser apresentados de forma concomitante com resultados de leituras dos pots anteriores, algo tipo:
P1xx P2yy P3zz P4ww Tx10000000 Rx10000000

Pode parecer algo inútil, mas será útil para desenvolvimento, testes de produção e campo.

### 6.2.3. Funcionamento do Driver de Motor

Este teste consiste em realizar sequências de testes do motor que permitam avaliar o driver e o motor, um de cada vez.

O teste do driver é realizado com um motor OK e o teste do motor é realizado com um driver já validado.

Os pots tem os seguinte significado:
P1 define disparos por minuto, na faixa de 8 a 30
P2 define o PWM aplicado na faixa de 30 a 100%, começar com mínimo
P3 define tempo de acionamento CW e CCW

Obs: não há fim de curso por software, mas pode ser implementado por hardware se estiver ligado na alimentação do motor. Uma sugestão é hackear o amplificador de corrente, provocando parada por percepção de curto.

No caso de ser um driver de relés P2 não vai influenciar nada, dev ser realizada alteração de corrente mediante regulagem de tensão da fonte específica do motor, mandatória no caso de relés.

Estes testes podem ser utilizados como testes “Open Loop” para ajudar o mapeamento de pressões de funcionamento e outros necessários para a implementação do sistema.

O FlexLed é da etapa anterior acrescido da etapa do motor e da corrente envolvida, reportado como Mxx Iyy, ficando assim:
Mxx P1xx P2yy P3zz P4ww Tx10000000 Rx10000000 Iyy

A sequência do Motor xx reportada em Mxx é a seguinte:
00: motor em repouso, aguardando start (=motor stop CCW)
01: motor start, movimento CW - Clockwise ou sentido de compressão do AMBU (A+ B-) 02: motor regime CW

Doc.: RDSV200330 EAR System Developer's FW Guide PTBR R00 | 7/7

03: motor final CW
04: motor stop CW
05: motor start, movimento CCW - Counterclockwise ou descompressão do AMBU (A- B+)
06: motor regime CCW
07: motor final CCW

O valor de PWM em cada etapa Mxx deve ser parametrizável. Isto será necessário para o mapeamento.

A corrente do motor Iyy, yy é obtido da mesma forma que a leitura dos pots, se trata dos 8 bits mais significativos da leitura do amplificador de corrente do motor. Correntes acima de um threshold programável (ex: 3 amperes terá Vadc correspondente a aproximadamente 1,29V) devem ser reportados por uma piscada de 200ms no led vermelho em D7.

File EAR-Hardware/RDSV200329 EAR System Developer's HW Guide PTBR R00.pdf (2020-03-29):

Doc.: RDSV200329 EAR System Developer's HW Guide PTBR R00 | 1/17

_____________________________________________________________________________

| Data | Signatures
Author: | 29/03/2020 | | Títle: Guia do Desenvolvedor Sistema EAR - Hardware
Verif.:

Aprov.:

### 1. Escopo

O objetivo deste documento é descrever o sistema EAR sob o ponto de vista de um desenvolvedor do hardware e como base para o desenvolvedor de software entender o sistema EAR. Para a mecânica e o “Firmware” serão criados documentos específicos. Este documento reúne especificações, recomendações e sugere componentes existentes e disponíveis para compor o sistema. Este documento também procura incluir documentos emitidos anteriormente para facilitar o acesso às informações.

Estão previstas ampliações de escopo do projeto para suportar respiração assistida, Somente para os pacientes em fase de recuperação. A eletrônica do projeto EAR já contempla expansões para esta função e outras.

Este projeto pode ser alterado a qualquer momento, sem aviso prévio.

Disclaimer: não assumimos nenhuma responsabilidade sobre qualquer dispositivo construído a partir das informações deste documento e orientamos para que os dispositivos sejam projetados na estrita observância às normas locais, que sigam as recomendações de especialistas e que sejam homologados pelas agências reguladoras em todas as fases.

### 2. Controle do Documento

- 29/03/2020: Emissão R00 – Português BR

### 3. Referências

- Open Source COVID19 Medical Supplies facebook: https://www.facebook.com/groups/670932227050506/
- COVID-19 Air BRASIL - Fast production of assisted ventilation devices https://www.facebook.com/groups/235476464265909/
- RDSV200320 Emergency Automatic Respirator Specification R00 – Preliminary
- RDSV200322 EAR Hardware Proposition Draft R00 – PTBR
- MIT E-Vent – “Key Ventilation Specifications”

### 4. Considerações Iniciais

Abreviaturas e termos utilizadas em todo o documento:
- EAR: Emergency Automotic Respirator
- FDC: Fim de Curso

Doc.: RDSV200329 EAR System Developer's HW Guide PTBR R00 | 2/17
- BAG: bolsa de ar, pode ser a do AMBU ou a do FIO2
- AMBU: Equipamento médico existente, utilizamos somente o BAG para comprimir ar para o paciente
- FIO2: Fraction of Inspired O2 define a proporção de O2 no ar inspirado pelo paciente
- ECU: Electronic Control Unit
- PEEP: Pressão positiva expiratória final. Para eletrônicos e SW developers, se trata de um “Offset DC” na pressão do ar do pulmão do paciente. A pressão nunca cai a menos de 5-10cm de H20.
- HEPA: tecnologia empregada em filtros de ar com alta eficiência na separação de partículas (wikipedia)
- NPN: polaridade da conexão do sensor ou atuador, comuta ou é comutado pelo GND (Low Side)
- SPI: Serial Peripheral Interface, interface serial síncrona, baseada em registradores de deslocamento
- WIP: Work in Progress, trabalho não finalizado
- GPIO: General Purpose IO, ou porta de uso geral do arduíno
- SOA: Safe operating area, ou área de operação segura do componente

Existem várias soluções de automação de AMBU, porque mais uma? A razão é simples: todas as automações de AMBU foram baseadas em materiais de disponibilidade em centros de pesquisa, não em municípios de menor renda. Sim, os 60% de municípios brasileiros que não dispõem de ventilador mecânico provavelmente não disporão dos insumos para produzi-los ou mantê-los neste primeiro momento.

O foco então se trata de um equipamento para regiões sem recursos, principalmente em países emergentes. Trata-se então do já difundido conceito de ter uma mão mecânica para apertar um AMBU. Esta mão mecânica é composta de um mecanismo de compressão mecânico movido por um motor de máquinas de vidro de automóveis, que já conhecemos e utilizamos em escala em produtos. Conhecemos os modos de falha do motor e os estamos tratando. O motor de vidros tem mecânica adequada para suportar reversões em cada ciclo, necessárias para o controle da quantidade de ar e da pressão aplicada ao paciente. Isto é possível devido ao mecanismo de sem-fim acoplado a ume engrenagem e um coupler de borracha interno. Já testamos um acionador mecânico que comprime um AMBU fechado e abre a válvula de segurança alimentado em 12V. AMBUs abertos conseguimos comprimir com 4Vdc.

Para o controle do sistema foi desenvolvida um módulo de controle – a ECU EAR - que pode ser montada e construída por qualquer pessoa que fabrique artesanalmente equipamentos eletrônicos. Existem versões com placas de circuito impresso face simples, para que possa ser produzida até por processos artesanais. Para alteração dos parâmetros, esta placa tem controles por potenciômetros para permitir uso fácil pelos profissionais de saúde. O microcontrolador é um Arduíno, similar ao da solução do MIT, que tem a maior base de desenvolvedores no mundo. Esta placa tem várias proteções, inclusive contra curto-circuito no motor, que entra em curto após uso prolongado. Esta placa também controla a velocidade do motor, definindo a pressão aplicada no AMBU. O uso do motor é reversível, para possibilitar o controle de deslocamento de compressão do AMBU, permitindo a variação do ar inspirado, ou volume tidal. A placa também possui várias entradas e saídas para acionamento direto de relés e leitura de sensores NPN.

Doc.: RDSV200329 EAR System Developer's HW Guide PTBR R00 | 3/17

O “firmware” a que se refere esta especificação é, a princípio, executado no Arduino Pro Mini.
Se o hardware for diferente, por favor buscar a documentação do hardware para sua versão de placa.

### 5. Requisitos Básicos

Requisitos básicos a serem atendidos, de acordo com: MIT-KVS: Key Ventilation Specification do MIT

- BPM (respirações por minuto):
- MIT-KVS: 8-30BPM
- Volume Tydal - quantidade de ar a ser administrado ao paciente:
- MIT-KVS: 200-800ml baseado no peso do paciente
- I/E ratio (relação tempo de inspiração / tempo de expiração):
- MIT-KVS: começar entre 1:2, melhor se ajustável entre 1:1 e 1:4
- Pressão máxima:
- limitada a 40cm H2O em qualquer condição, recomendada válvula passiva de alívio fixa em 40cm H2O
- pressão de platô limitada a, no máximo, 30 cmH20
- PEEP é necessário de 5-15 cm de H2O, muitos pacientes precisam 10-15 cm de H2O

### 6. Visão Global do Sistema EAR

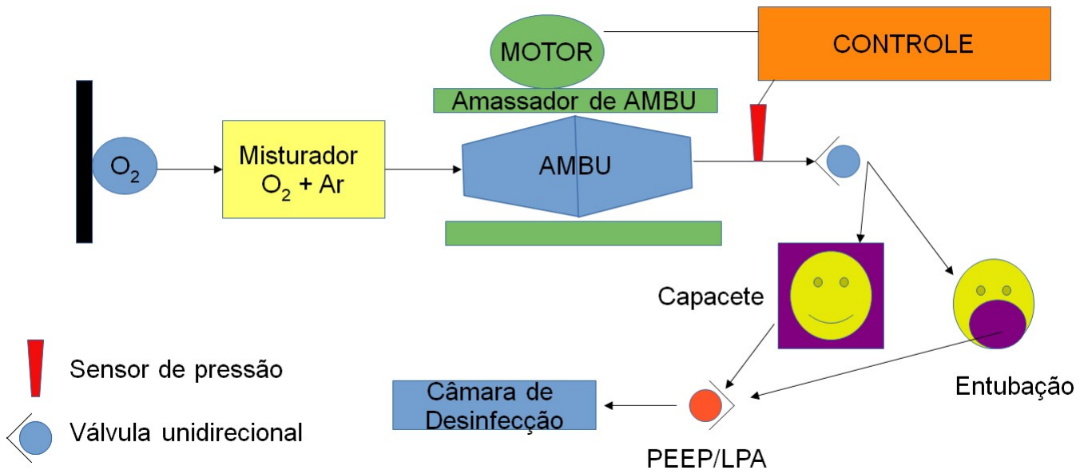
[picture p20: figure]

Esboço do sistema EAR, desenho by Suzuki

O processo controlado pode ser implementado da seguinte forma:

Doc.: RDSV200329 EAR System Developer's HW Guide PTBR R00 | 4/17
- Mistura por válvulas mecânicas especializadas ou eletroválvulas pneumáticas a partir de duas fontes: O2 comprimido e ar comprimido. A mistura pode ser controlada pela ECU

– Compressão da Bolsa de AMBU ADULTO por um mecanismo motorizado com reversão. O controle de volume Tydal é realizado mediante controle de curso e a pressão máxima é realizada por controle da velocidade do motor. Estamos trabalhando em conjunto com desenvolvedores para termos bolsas para reposição, pois prevemos que estourem pelo uso contínuo. Em caso de rompimento de bolsa, quebra de motor ou dano de algum componente mecânico todo o conjunto compressor de AMBU pode ser substituído em menos de 5 segundos.

– Acoplamento ao paciente, método não invasivo: usa máscara de AMBU com válvula unidirecional adicional para evitar retorno ao AMBU do ar contaminado e encaminha para uma câmara descontaminante o ar expirado pelo paciente. Controle de Peep mandatório. Capacete com pressão negativa se disponível. Respiração assistida prevista no escopo do projeto.

- Acoplamento ao paciente – método invasivo: nesta etapa está prevista ventilação não assistida com uso de mangueira intratraqueal em pacientes sedados. Haverá monitoração de pressão positiva com alerta para detecção de expiração conflitante pelo paciente.

Utilizamos máscara de AMBU com mangueira e válvula para evitar retorno ao AMBU do ar contaminado e que encaminhe para uma câmara descontaminante o ar expirado pelo paciente. Peep mandatório. Capacete com pressão negativa se disponível.

- Controle de PEEP

Haverá controle de PEEP por filtro de barreira HEPA ou similar, associado ou não a uma restrição mecânica para controle de pressão de PEEP. Caso não existe filtro de barreira, será mandatória exaustão ou câmara de descontaminação.

Obs: haverá um medidor permanente de pressão de PEEP, mecânico ou eletrônico.

- Exaustão do ar contaminado

Esta etapa será mandatória se o ar expirado pelo paciente não passar por filtro de barreira. Podem ser aplicadas as soluções abaixo isoladamente ou em conjunto.

- Passagem forçada por descontaminantes químicos ou mecânicos. Podem ser utilizadas soluções com sabão, que aderem às gorduras do Covid19, ou água sanitária (fonte abundante de hipoclorito de sódio ou cálcio) em concentrações adequadas.
- Aquecedores por queima. Para submeter o vírus a altas temperaturas. Podem ser utilizadas serpentinas para aquecimento de água onde o ar passaria dentro, usar o ar expirado em chaminés com queima de madeira ou gás, junkers, etc
- Irradiação UV: o Covid19 poderia ser submetido a UV de alta intensidade. Seria necessário um tempo de exposição de muitos minutos mesmo com fontes de alta intensidade

Doc.: RDSV200329 EAR System Developer's HW Guide PTBR R00 | 5/17

Todo o setup acima pode ser alimentado por baterias automotivas carregadas pela rede AC, para prover energia mesmo que caia a rede AC ou por uma fonte DC de 12V, 30 ampéres ou maior, destas utilizadas para alimentar iluminação de Leds, encontráveis em casas de eletrônica ou iluminação.

### 7. Visão Geral do Hardware Controlado pelo Sistema EAR

O Projeto EAR nasceu com conceito de compressão de AMBU pneumática, mas o conceito foi abandonado porque exigiria ar comprimido e porque o volume de ar não pode ser controlado facilmente. O conceito foi trocado para compressão mecânica de AMBU.


Compressor de AMBU projeto MIT E-Vent

A arquitetura do sistema é muito similar ao do projeto MIT E-Vent, que conheci alguns dias depois de esboçar o Projeto EAR, muitas coisas são idênticas, aproveito a imagem do MIT que é muito bem feita.


Arquitetura do projeto MIT E-vent

Doc.: RDSV200329 EAR System Developer's HW Guide PTBR R00 | 6/17

Listamos abaixo as diferenças principais da arquitetura do E-Vent e o EAR

- a ECU EAR usa Arduino Pro Mini, por questões de disponibilidade local. Pode usar a princípio qualquer Arduíno, mas tem que fazer uma PCB adaptadora para acoplar na ECU EAR ou ligar por fios, somente para desenvolvimento.
- o projeto EAR prevê a possibilidade de fazer controle de FIO2 a partir de eletroválvulas pneumáticas de caminhão, mediante controle de tempo de acionamento individual, com armazenamento em uma almofada plástica de vinyl, doravante denominada simplesmente BAG. Enchemos parcialmente o BAG (ex: 80% ou menos) que será esvaziado apenas parcialmente (ex: máximo 30%) em cada admissão do AMBU. Existem sensores de FDC para inibir as válvulas se o BAG estiver a 80%. Para que o EAR possa aplicar a quantidade correta, existe um modo de configuração onde definimos os tempos de acionamento de cada válvula pelos mesmos pots de operação, pelo menos nesta fase inicial. Sugerimos marcas visuais no painel dos pots para memorizar esta configuração.
- o motor do EAR é um motor BDC de máquinas de vidro de automóveis, do tipo utilizado no Pálio e Gol, o motor robusto com maior disponibilidade local. Acredito que a vida útil é superior ao do E-Vent que parece ser um motor BDC com engrenagens planetárias enquanto o motor de vidros é um sem-fim com coupler interno, próprio para reversões.

O motor de vidros tem mecânica espelhada para lado direito e esquerdo, prever a montagem de qualquer tipo no hardware.

O motor de vidros não dispõe de encoder, deve ser adicionado externamente um sensor. Uma possibilidade é o “speed sensor” utilizado em automóveis. Caso a adaptação mecânica não seja possível, verificar o número de pulsos por revolução, extrair o ímã multipolar, colá-lo em alguma parte girante e posicionar o sensor hall de forma adequada.

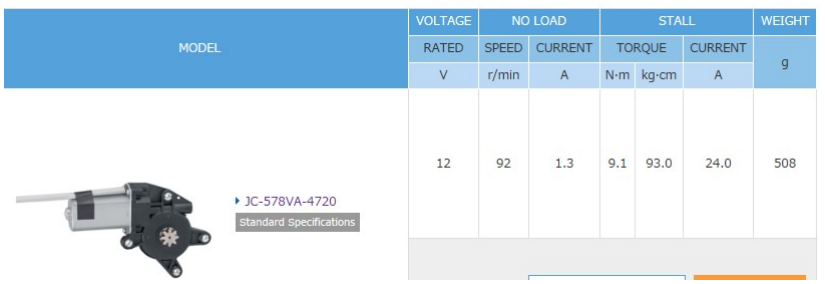
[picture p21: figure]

Motor do EAR: Mabuchi, utilizado nos carros de passeio

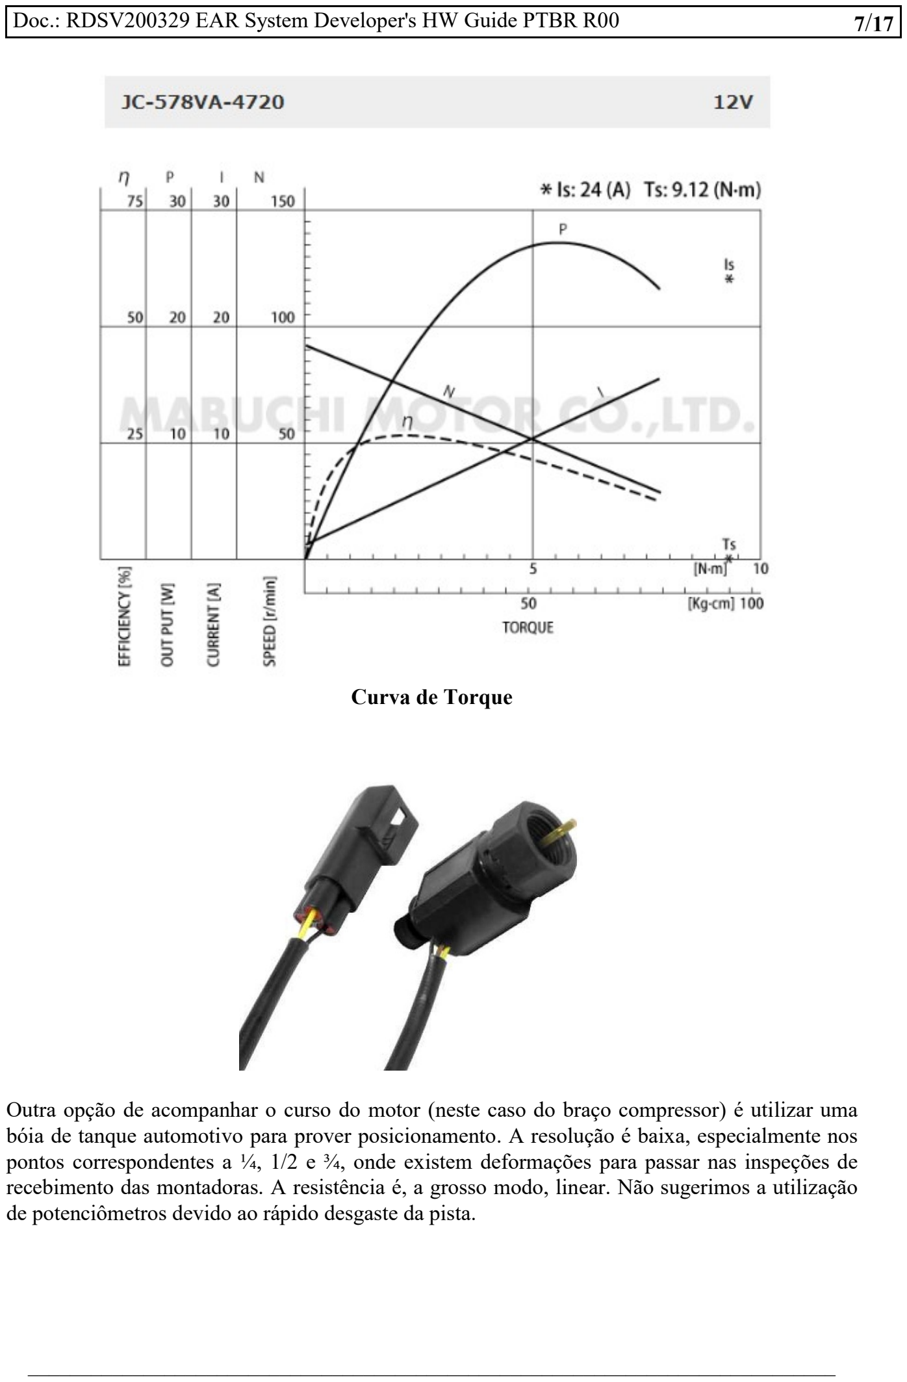
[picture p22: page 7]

Doc.: RDSV200329 EAR System Developer's HW Guide PTBR R00 | 7/17

Curva de Torque

Outra opção de acompanhar o curso do motor (neste caso do braço compressor) é utilizar uma bóia de tanque automotivo para prover posicionamento. A resolução é baixa, especialmente nos pontos correspondentes a ¼, 1/2 e ¾, onde existem deformações para passar nas inspeções de recebimento das montadoras. A resistência é, a grosso modo, linear. Não sugerimos a utilização de potenciômetros devido ao rápido desgaste da pista.

Doc.: RDSV200329 EAR System Developer's HW Guide PTBR R00 | 8/17
- o projeto EAR não dispõe de monitor de pressão neste primeiro momento, sugerimos um monitor mecânico ou eletrônico. Pode ser agregado um display ao projeto posteriormente, via serial ou SPI. O sensor de pressão está previsto, mas com P/N TBD.
- para acionar o motor não utilizamos o motor driver shield, por disponibilidade. Usamos relés na versão mais simples e na versão mais complexa utilizamos mosfets discretos, dos tipos utilizados em armas Airsoft, ECUs e amplificadores automotivos. Quando usamos relés controlamos a pressão máxima através de uma fonte externa, ajustável, que varia a tensão aplicada ao motor. Os mosfets trabalham com PWM variável.
- No E-Vent temos a mistura de Ar e O2 (FIO2) realizada externamente e aplicada diretamente ao AMBU. No EAR temos a mistura realizada pelo EAR, mediante controle de válvulas pneumáticas de caminhões 12V.
- o Projeto EAR tem expansão de IOs, por módulos. Cada módulo proporciona 8 entradas para sensores NPN e 8 saídas para relés com acionamento NPN.

Vamos então discorrer sobre os diversos componentes do hardware. Serão acrescentadas referências de fabricantes ou distribuidores locais, na medida do possível.

### 7.1. ECU EAR

A ECU EAR, por se tratar de um projeto inclusivo, foi projetada com placas de circuito impresso face simples, com tecnologia PTH.

Em função de disponibilidade de PCBs em placas 10x10cm nos varejo, a ECU EAR foi dividida em 3 placas: CPU, IO Lento e Driver do Motor


Doc.: RDSV200329 EAR System Developer's HW Guide PTBR R00 | 9/17

### 7.1.1. CPU ECU EAR

A CPU EAR contém o Arduíno, a fonte de 5V interna, potenciômetros, leds e conectores para as demais placas. A conexão entre as placas é realizada por meio de IDCs (flat cables) que podem ser obtidos de computadores.

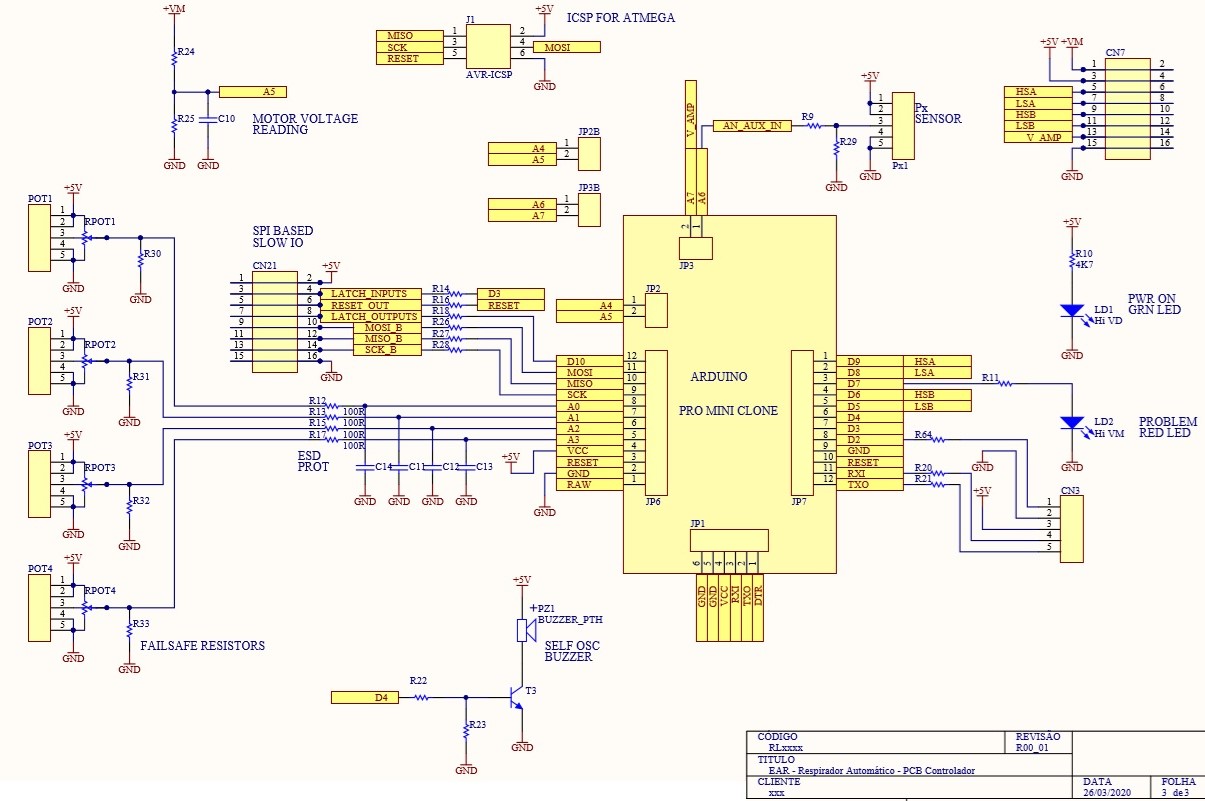
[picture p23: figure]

### 7.1.1.1. Arduino

Para informações, favor consultar os documentos de referência. O Arduino referência utilizado para este projeto foi um clone do Arduino Pro Mini 5V 16 MHz, mostrado abaixo.

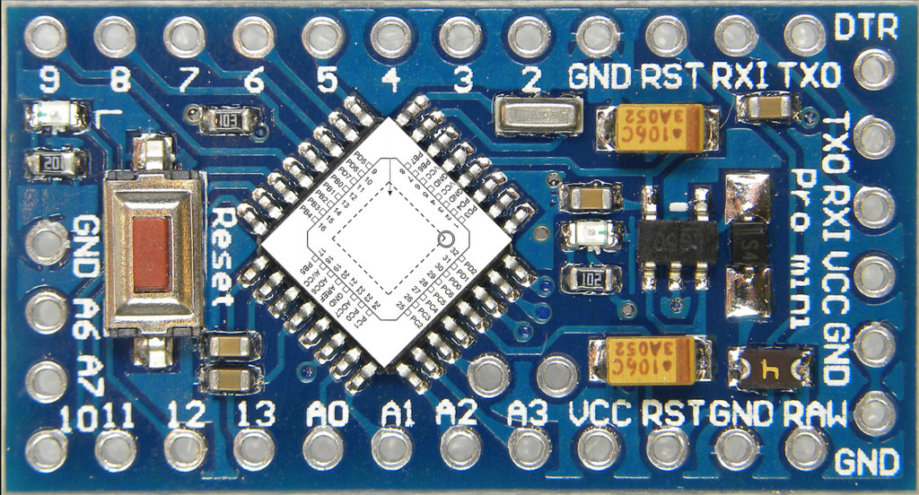
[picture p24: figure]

Outros Arduinos podem ser utilizados, desde que respeitadas as funcionalidades e o firmware seja contruído ou adaptado para a variação escolhida. Para contornar a baixa disponibilidade de IOs do Arduino Pro Mini, implantamos um expansor de IO baseado em SPI, implementado por CIs 74HC595 e 74HC165. Este expansor em sua versão mais básica disponibiliza 8 saídas para

Doc.: RDSV200329 EAR System Developer's HW Guide PTBR R00 | 10/17

acionamento NPN com capacidade para acionamento direto de relés e 8 entradas para sensores NPN, contato seco de relés. A interface de expansão pode ser multiplicada, mas é limitada na prática pela degradação dos sinais SPI. Já implementamos anteriormente com sucesso 16+16 IOs.

Tabela de PINOUT e funcionalidade do Arduino. Todos os sinais GPIO são ativos em +5V exceto se especificado em contrário.

PINO | FUNÇÃO PINO | OBSERVAÇÕES
TXO | TXO | Tx Bootloader, monitor serial ou TxD Rede
RXI | RXI | Rx Bootloader, monitor serial ou RxD Rede
RST | /RESET | Reset geral, para acionamento usar open collector NPN
GND | GND | GND
D2 | GPIO | Reservado Rede_RTS
D3 | GPIO | Latch Inputs expansor de IO – SH /LD 74HC165
D4 | GPIO | Buzzer OUT
D5 | GPIO | Motor Low Side B
D6 | PWM | PWM Motor Hi Side B
D7 | GPIO | Checklamp LED Vermelho
D8 | GPIO | Motor Low Side A
D9 | PWM | PWM Motor Hi Side A
D10 | GPIO | Latch Outputs expansor de IO – RCK 74HC595 +Edge
D11 | MOSI | MOSI expansor de IO
D12 | MISO | MISO expansor de IO
D13 | SCK | SCK expansor de IO – normalmente ligado a um LED
A0 | AN0 | Leitura Analógica POT1
A1 | AN1 | Leitura Analógica POT2
A2 | AN2 | Leitura Analógica POT3
A3 | AN3 | Leitura Analógica POT4 ou futura entrada Multiplex AN
VCC | VCC | +5V
RST | /RESET | Reset geral, para acionamento usar open collector NPN
GND | GND | GND
RAW | RAW | Não Conectado – Recomendado remover o regulador interno do Arduíno.
A7 | AN7 | Leitura Analógica Corrente do Motor
A6 | AN6 | Leitura Analógica Elemento Externo (ex: Sensor Pressão)
A5 | AN5 | Leitura V_Motor após PPTC
A4 | AN4 | Reservado

O pinout para conexão para interface serial/PC via conversor USB TTL será utilizado diretamente para gravação a partir de Bootloader. Optamos por este tipo de Arduíno sem conversor USB TTL embutido porque podemos implementar posteriormente uma rede local com fio, provavelmente com isolação galvânica, para interligar os módulos Arduíno.

Doc.: RDSV200329 EAR System Developer's HW Guide PTBR R00 | 11/17

Como não há padronização nos clones de Arduíno quanto ao pinout de A4 a A7, estes sinais serão disponibilizados na placa fora do footprint do Arduíno, para conexão mediante fios que sugerimos que sejam realizados com “wire-wrap” por baixo da placa

### 7.1.2. Módulos de IOs Lentos

- o Projeto EAR tem expansão de IOs lentos, via SPI, por módulos. Cada módulo proporciona 8 entradas para sensores NPN e 8 saídas para relés com acionamento NPN. Denominamos lentos porque não serão frequentemente lidos ou atualizados, as taxas vão depender da implementação de software específica, mas penso que devem ficar no range de 1 a 10 ms entre cada atualização. Um dos gargalos importantes é a leitura dos sensores que promovem o desligamento dos motores, quanto maior o tempo entre leituras, mais o motor irá se deslocar. Cuidado deve ser tomado para ter bufferização de todas estas saídas em software, porque as leituras das entradas sobreescrevem, SEMPRE, as saídas. Embora as saídas necessitem de um sinal de “Latch_Outputs” para serem efetivadas, um pequeno ruído elétrico pode promover isto.

No primeiro módulo de IO, denominado IO1, de uso mandatório, várias destas entradas estão alocadas, seguem exemplos, a serem posteriormente detalhados:

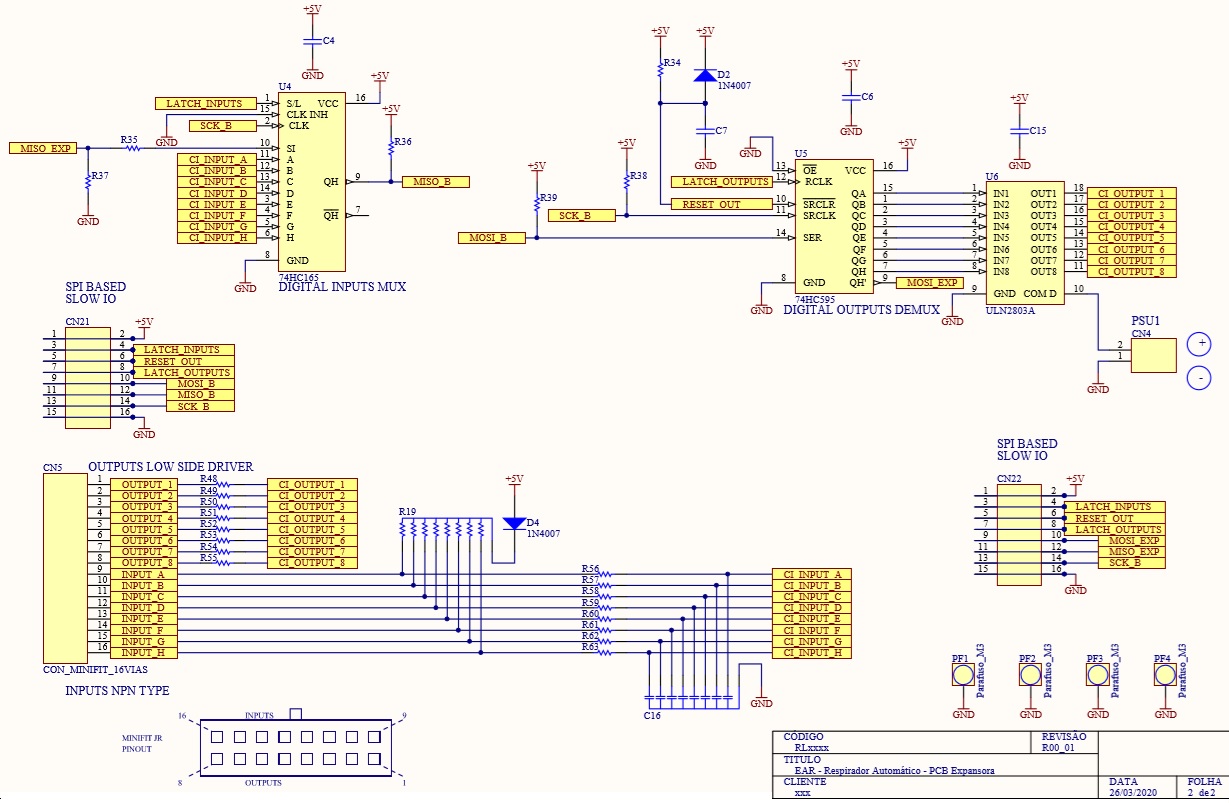
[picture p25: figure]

Já existem atribuições pré-definidas para entradas e saídas. Caso seja necessário trabalhar com entradas e saídas fora do até então previsto, por necessidades específicas, recomendamos que sejam utilizadas as últimas entradas e saídas existentes.

Doc.: RDSV200329 EAR System Developer's HW Guide PTBR R00 | 12/17

### 7.1.2.1. Entradas INx

As entradas lentas são entradas NPN, comutadas a GND, níveis de tensão HCMOS (se usado 74HC165) ou TTL (se usado 74HCT165). Podem estar abertas ou conectadas a GND. Tensões acima de +5V não são recomendadas e podem causar queima do 74HC(T)165, apesar de que existem resistores para limitar a corrente dos diodos de clamp das entradas do 74HC(T)165.

Entradas já definidas:
- IN1A: Chave SPST ou SPDT CONFIG/OPERATION, que define se estamos configurando ou operando o sistema. Segue um exemplo.

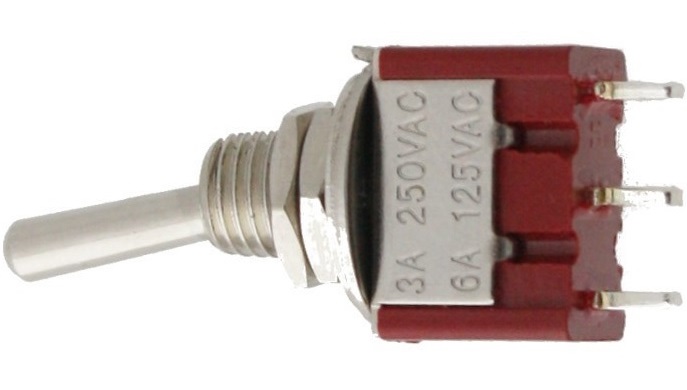
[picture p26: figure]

- IN1B: pushbutton START/SET, define se começa (operação) ou aceita config (configuração). Seguem exemplos.

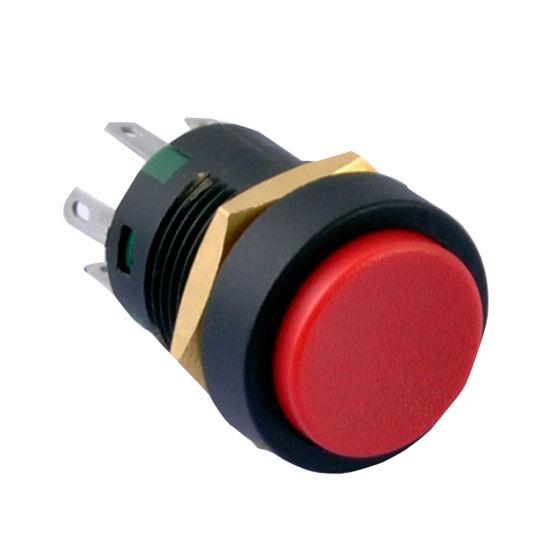
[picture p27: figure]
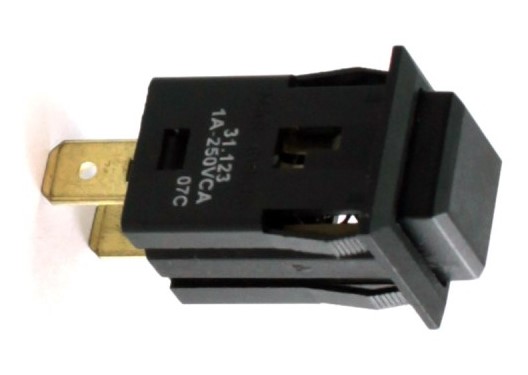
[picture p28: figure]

- IN1C: FDC (Fim de Curso) motor recolhido (AMBU em repouso), sugerimos utilizar duas chaves alavanca em série ou sensor hall + ímã. Cuidado: a operação pode ser diferente. Sugerimos que o estado seja programável porque o Hall será sensível na presença do ímã e as chaves podem operar assim também, mas se trabalhassem NF poderíamos perceber problemas com o cabo. Segue um exemplo.

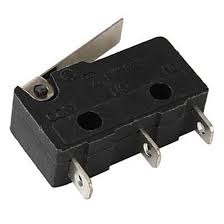
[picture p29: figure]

- IN1D: FDC motor expandido (AMBU totalmente comprimido), sugerimos utilizar duas chaves alavanca em série ou sensor hall + ímã. Cuidado: a operação pode ser diferente.

Doc.: RDSV200329 EAR System Developer's HW Guide PTBR R00 | 13/17

Sugerimos que o estado seja programável porque o Hall será sensível na presença do ímã
e as chaves podem operar assim também, mas se trabalhassem NF poderíamos perceber problemas com o cabo.
- IN1E: FDC BAG FIO2 Ar+O2 expandido (BAG quase cheio), sugerimos utilizar duas chaves alavanca em série ou sensor hall + ímã. Cuidado: a operação pode ser diferente. Sugerimos que o estado seja programável porque o Hall será sensível na presença do ímã e as chaves podem operar assim também, mas se trabalhassem NF poderíamos perceber problemas com o cabo.

### 7.1.2.2. Saídas OUTx-x

As saídas foram implementadas com ULN2803 ou ULN2003, que são drivers bipolares padrão com a maior disponibilidade. Permitem acionamento direto de relés, com as bobinas ligadas a V+ (tensão de alimentação positiva) e a saída correspondente. Estes drivers são especificados para 500mA, mas a potência tem que ser observada. Caso a corrente seja insuficiente, podemos colocar drivers em piggyback ou, melhor ainda, utilizar relés auxiliares.

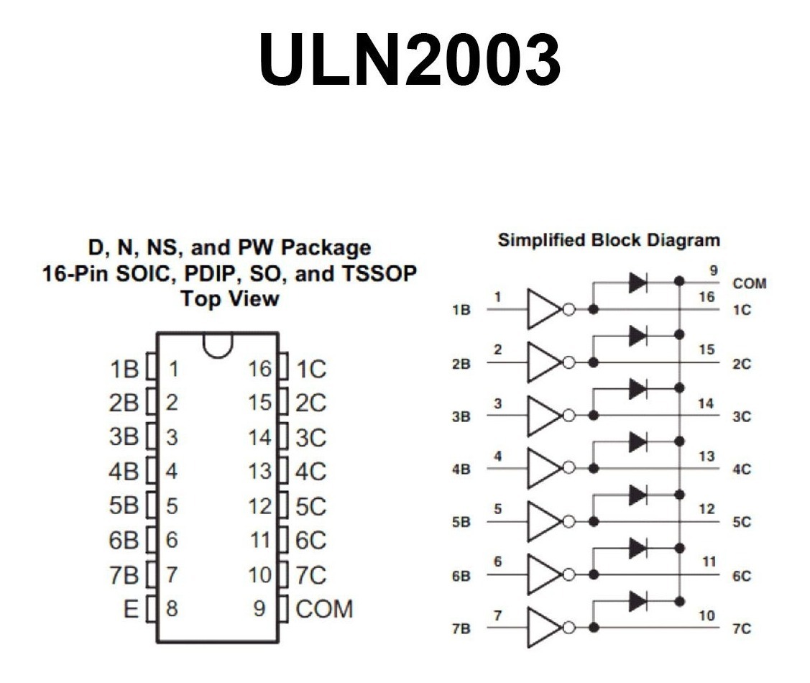
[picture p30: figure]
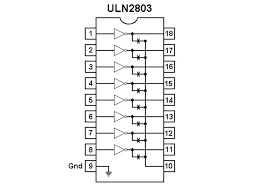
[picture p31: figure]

Dispositivos acima de 12V (ex: 24V) podem ser utilizados, mas não podem ser aplicados diretamente nas saídas OUTX-X porque estas saídas tem diodos de “kickback” para a fonte de 12V. Neste caso, sugerimos utilizar uma fonte extra de 24V e um relé auxiliar de 12V para comutar o dispositivo em 24V. Existem muitos reles auxiliares de fabricação local. Segue exemplo.

Saídas já definidas:

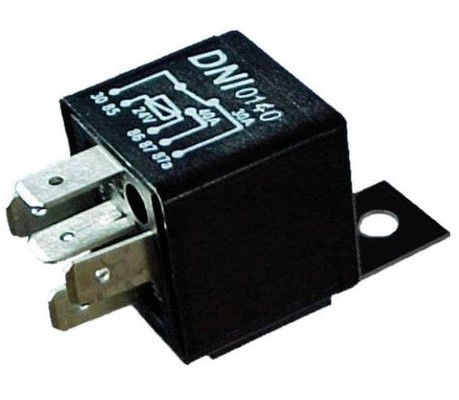
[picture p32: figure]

- OUT1-1 reservado. Pode não ser implementado no hardware, em função de disponibilidade do ULN2803, pode ser substituído pelo ULN2003 que tem somente 7 saídas.

Doc.: RDSV200329 EAR System Developer's HW Guide PTBR R00 | 14/17
- OUT1-2 acionador de sirene, ex: sirene automotiva 12V FKS ou similar. Necessário abafador mecânico adicional. Ex: almofadas aplicadas ao cone.

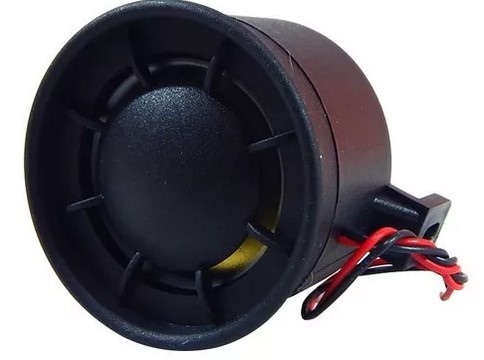
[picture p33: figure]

- OUT1-3 acionador eletroválvula O2 (para controle de FIO2), eletroválvula para ar comprimido de caminhões 12V. Ref Fluair 104-SL 1/4 12VCC, Thermoval tem diversos tipos, Parker tem várias possibilidades.

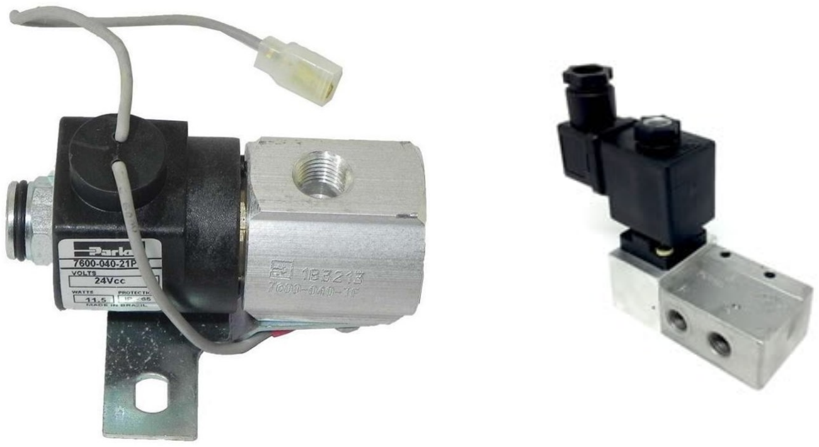
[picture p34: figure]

- OUT1-4 acionador eletroválvula Ar comprimido (para controle de FIO2), eletroválvula para ar comprimido de caminhões 12V, mesma válvula que a anterior. As saídas OUT1-3 e OUT1-4 podem também ser monitoradas externamente e eventualmente podem ser elementos de um sistema de watchdog muito lento, que poderia desligar todo o sistema.

### 7.1.2.3. Potenciômetros para ajustes

Os potenciômetros para o projeto EAR são os mais comuns encontrados, lineares, 10Kohms, encontráveis sob o nome genérico de B10K. O valor do potenciômetro não é crítico, valores na faixa de 220 Ohms a 47K devem funcionar. Como o Pot está ligado em +5V, GND e o wiper vai para o ADC, a leitura é ratiométrica. Nota ao pessoal de SW: não assumam que são lineares, porque o modelo montado será o encontrado, linear ou log, 1K, 5K, 10K, 22K... mas não importa muito porque quem fecha o laço de controle é o operador humano, que vai corrigir não-linearidades girando o botão.

Doc.: RDSV200329 EAR System Developer's HW Guide PTBR R00 | 15/17

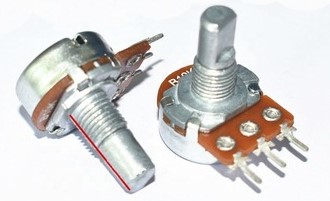
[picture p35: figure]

Estes potenciômetros possuem dupla função, dependendo do modo de trabalho. O modo é definido por IN1A em GND (Configuração) ou aberto (Operação).

Significado dos potenciômetros em modo Operação:
- P1 define BPM, respirações por minuto
- P2 define volume Tidal, volume de ar+O2 bombeado ao paciente
- P3 define taxa I/E, quociente tempo inspiração/tempo expiração
- P4 define limite de pressão máxima aplicada

Na operação o curso dos potenciômetros é restrito em 20% a 80% por questões de confiabilidade. O FMEA premiminar mostrou que os potenciômetros podem falhar e estas falhas provocam leituras próximas a 0 ou 100% (5V). O comportamento nas faixas de 0-10% e 80-100% é TBD. Opções seriam o último valor válido lido ou presets fixos pré programados (ex: 50%, fixo). De qualquer forma, alarmes serão gerados no BIP local e na sirene externa OUT1-1. Bloqueios mecânicos de curso podem ser considerados, como parafusos limitando o bico de “chickenhead pots”. Isto evita que em pânico o profissional de saúde use o potenciômetro fora da área útil. Recomendamos efetuar marcações de range máximo e mínimo, se possível.

Significado dos potenciômetros em modo Configuração:
- P1 BPM (fixo)
- P2 TBD (fixo?) Volume Tidal ?
- P3 define o tempo de acionamento da válvula de ar comprimido para controle de FIO2 (0-200ms), partindo do princípio que o tempo de acionamento da válvula de O2 é fixo, correspondente a 400ml (400ms). Lembrando que leitura zero seria 20% de curso.
- P4 TBD (fixo?)

TBD: Quando em modo Configuração, os Pots serão aceitos mediante um comando “SET” gerado a partir de um botão ligado entre IN1B e GND. Talvez o botão altere dinamicamente o significado dos potenciômetros de múltipla função. Exemplo: apertando o botão P3 passa a definir o tempo de acionamento da válvula de ar comprimido para controle de FIO2, armazena este valor em memória não volátil e ao soltar o botão retorna a função original. OU os pots só são atualizados em função do modo mediante um “enable”. Isto não é intuitivo para o profissional de saúde, o melhor seria se pudéssemos ter mais potenciômetros.

Doc.: RDSV200329 EAR System Developer's HW Guide PTBR R00 | 16/17

### 7.1.3. Driver do Motor

O driver do motor faz o acionamento do motor e retorna informação de corrente e tensão do motor para a CPU ECU EAR. Foram previstos dois modos de acionamento, via relés e mosfets. Em ambos os casos, a corrente do motor pode ser lida pela CPU mediante um shunt de 100mR, 2512 ou PTH, e uma amplificação por um amplificador operacional. A proteção de curtos é híbrida, ou seja, opera por hardware por períodos pequenos de tempo (alguns milissegundos para os mosfets) e se faz necessário que o software aborte acionamento em caso de curto prolongado.

### 7.1.3.1. Driver do Motor utilizando relés

O driver que utiliza relés é o mais simples, mas exige uma fonte de alimentação adicional, que pode ser uma fonte de bancada. Possui limitações, como a corrente do motor é definida somente pela tensão de alimentação da fonte adicional, ou seja, não há controle dinâmico de corrente, nem controle da pressão resultante. As vantagens são a simplicidade e facilidade de obtenção e troca dos relés padronizados T73. Recomendamos relés de fabricantes homologados ISO/TS 16949, mas na falta destes, usar relés como o da foto e prever menor período entre trocas.

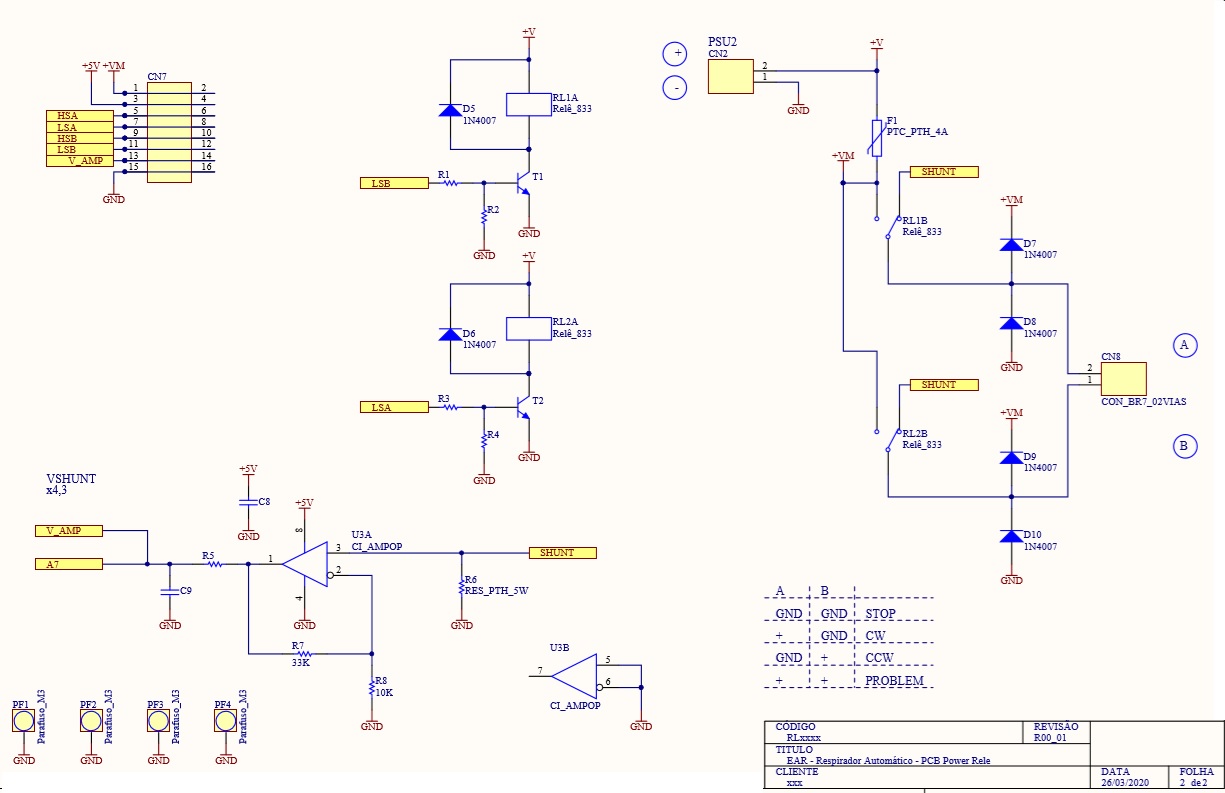
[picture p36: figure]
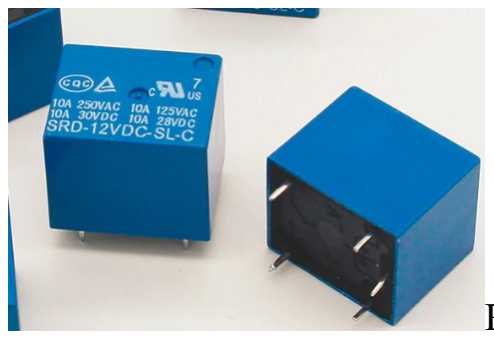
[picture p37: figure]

Relé T73

Doc.: RDSV200329 EAR System Developer's HW Guide PTBR R00 | 17/17

### 7.1.3.2. Driver do Motor utilizando mosfets

Este driver ainda está em WIP. Utiliza mosfets canal N, low level drive, preferencialmente automotivos. A versão apresentada usa mosfets canal P e N, estamos trabalhando para utilizar somente canal N, em DPAK ou TO220. O controle é por PWM no HiSide e GPIO no low side da Ponte H. A tensão do shunt é amplificada para envio à CPU. Em caso de curtos, é importante: detectar, limitar o tempo em curto de acordo com a SOA do mosfet, registrar a falha, sinalizar o problema, desligar se exceder o tempo programado, esperar esfriar e tentar religar novamente. Maiores detalhes serão apresentados no EAR System Developer’s SW Guide, a ler publicado.

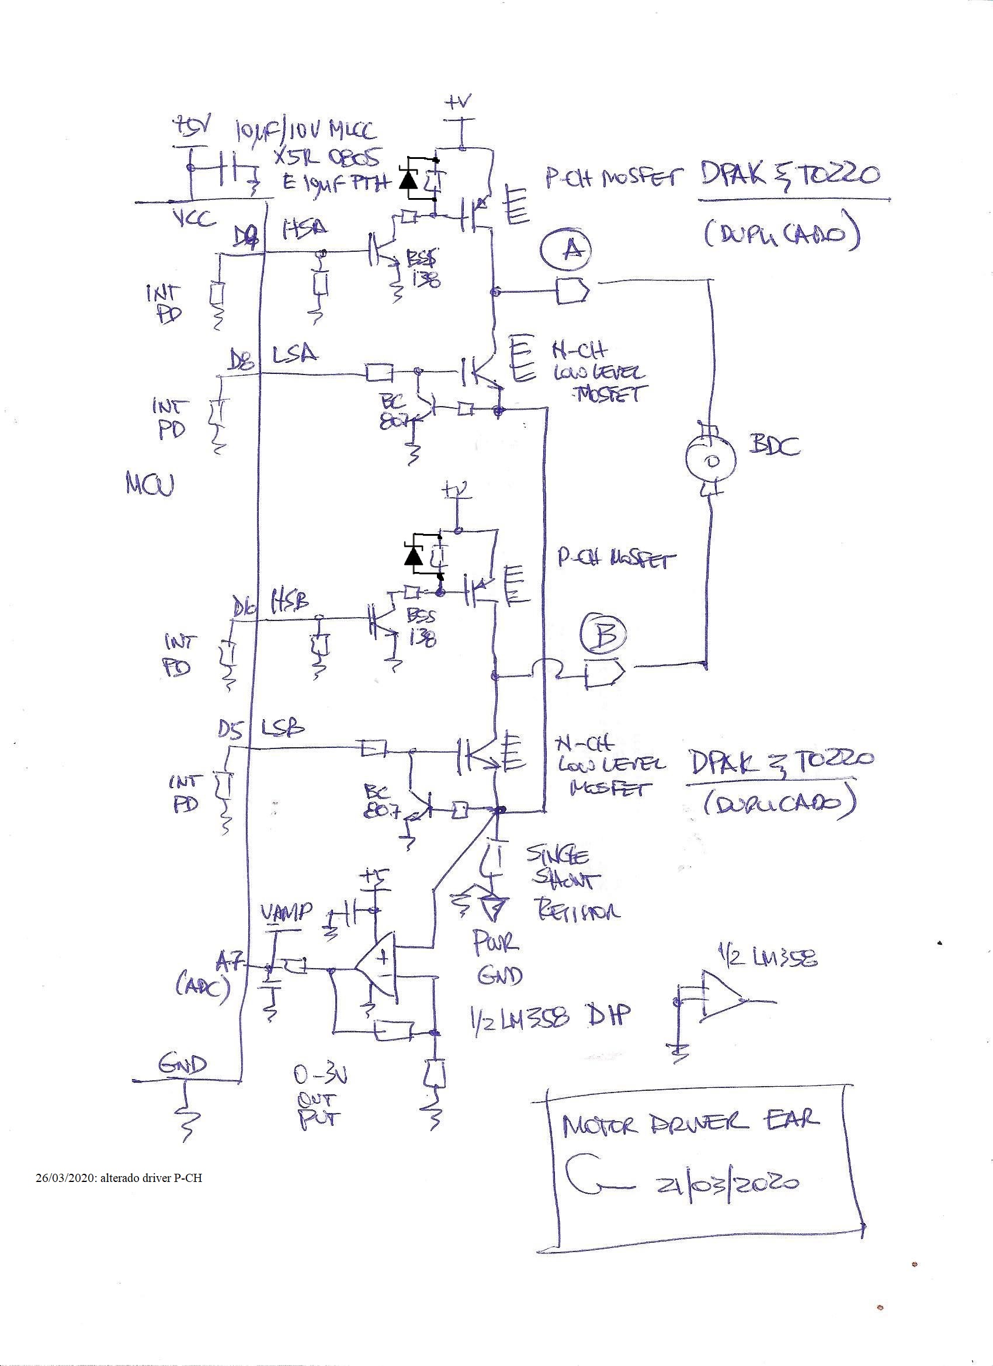
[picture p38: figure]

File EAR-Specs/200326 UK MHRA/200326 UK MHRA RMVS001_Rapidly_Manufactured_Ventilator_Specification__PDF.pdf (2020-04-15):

# Rapidly Manufactured Ventilator System (RMVS)

Document RMVS001 - Specification

Issued by MHRA

Introduction

This is a specification of the minimally (and some preferred options) clinically acceptable ventilator to be used in UK hospitals during the current COVID-19 pandemic caused by SARS-CoV-2 virus. It sets out the clinical requirements based on the consensus of what is ‘minimally acceptable’ performance in the opinion of the anaesthesia and intensive care medicine professionals and medical device regulators. It is for devices, which are most likely to confer therapeutic benefit on a patient suffering with ARDS caused by SARS-CoV-2, used in the initial care of patients requiring urgent ventilation. A ventilator with lower specifications than this is likely to provide no clinical benefit and might lead to increased harm, which would be unacceptable for clinicians.

Intensive care medicine is a whole system of care and ventilators cannot be safely used on any patient without trained staff and other equipment and medicines. Where these impinge on the specification they are mentioned below.

It is proposed these ventilators would be for short-term stabilisation for a few hours, but this may be extended up to 1-day use for a patient in extremis as the bare minimum function. Ideally it would also be able to function as a broader function ventilator which could support a patient through a number of days, when more advanced ventilatory support becomes necessary.

Ventilation

1. At least 1, optionally 2 modes of ventilation
a. Must have mandatory ventilation.
b. Mandatory mode must be either (ideally) Pressure Regulated Volume Control, or a pressure controlled ventilation (PCV) or a volume controlled ventilation (VCV).
c. PRVC/Pressure Controlled - a set pressure is delivered for the period of inspiration and the volume achieved is measured and displayed. Ideally PRVC, an adaptive mode where the tidal volume is set and the lowest possible pressure is delivered to achieve this volume. Pressure Control Ventilation where the user has to provide the adaptive control to achieve tidal volume is only acceptable if the tidal volume delivered is clearly displayed and the user can set patient specific upper and lower tidal volume alarms to alert to the need to adjust the pressure.
d. Volume Control – the user sets a tidal volume and respiratory rate. The tidal volume is delivered during the inspiratory period. Acceptable only if additional pressure limiting controls are available, see Inspiratory Pressure section.
e. Optional pressure support mode for those patients breathing to some extent themselves, e.g. BIPAP or SIMV-PC. The user sets an inspiratory pressure and an expiratory pressure. The ventilator can sense when a patient starts to breathe in and apply the inspiratory pressure, then sense when the patient starts to breathe out and apply the expiratory pressure (this pressure is still positive but lower than the inspiratory pressure).
2. If the patient stops breathing in a spontaneous mode it must failsafe automatically onto mandatory ventilation.
3. Inspiratory airway pressure, the higher pressure setting that is applied to make the patient breathe in:
a. Plateau pressure should be adjusted to achieve volume and be limited to 35 cmH2O by default. It is acceptable if an option to increase this to 70 cmH2O in exceptional circumstances is provided
b. Peak pressure should be no more than 2 cmH2O greater than plateau pressure.
c. If volume control ventilation is used, the user must be able to set inspiratory airway pressure limit in the range at least 15 – 40 cmH2O in at least increments of 5 cmH2O.
d. There must be a mechanical failsafe valve that opens at 80 cmH2O.
4. Positive End Expiratory Pressure (PEEP). The pressure maintained in the breathing system during expiration.
a. Range 5-20 cm H2O adjustable in 5 cmH2O increments.
b. Patient breathing system must remain pressurised to at least the PEEP level setting at all times.
5. Inspiratory:Expiratory ratio (I:E). The proportion of each breathing cycle that is spent breathing in compared to breathing out.
a. 1:2.0 (i.e. expiration lasts twice as long as inspiration).
b. Optionally adjustable in the range 1:1 – 1:3.
6. Respiratory Rate. The number of breathing cycles every minute.
a. Range 10 – 30 breaths per minute in increments of 2 (only in mandatory mode) can be set by the user.
7. Tidal Volume (Vt) setting, if provided. The volume of gas flowing into the lungs during one inspiratory cycle
a. Must have at least one setting of 400ml +/- 10 ml.
b. Ideally 350ml and 450 ml options.
c. Optionally Range 250 – 600 ml in steps of 50ml.
d. Even more optionally up to 800 ml.
e. Optionally the ability to input body weight and have volume calculated as e.g. 6ml/kg of ideal body weight.

Gas and electricity
1. Incoming Gas Supply.
a. All gas connectors and hoses must comply with BS EN ISO 5359:2014+A1:2017, ISO 5359:2014/AMD 1:2017 and BS 2050: 1978 Electrical Conductivity.
b. Must connect to wall pipeline oxygen supply via BS 5682:2015 compatible probes (Schrader). If hose not permanently fixed to machine, then must connect with NIST (Non-Interchangeable Screw Thread to ISO 18082:2014/AMD 1:2017). Oxygen pipeline pressure is approximately 3.7 – 4.5 bar.
c. Oxygen supply from wall outlets outside of ICU and theatres is limited to approximately 6-10 lpm (HTM_02-01_Part_A) and so provision for a gas reservoir will be required to manage peak inspiratory flow rates of up to 100 lpm
d. Average oxygen consumption must be no more than 3 lpm. This may be allowed to increase as greater certainty is gained over oxygen supply.
e. Optionally can connect to wall pipeline Medical Air (MA4, NOT SA7) via BS 5682:2015 compatible probes.
f. Optionally can connect to ISO 7396-2:2007 compatible Anaesthetic Gas Scavenging System or an external activated charcoal absorber (If inhaled anaesthetic agents are being used).
g. Optionally can operate using an oxygen concentrator device for input oxygen, these will typically be limited to 10 lpm.
2. Electricity Supply.
a. Should connect to 240V mains.
b. Should be PAT tested to the adapted IEC 60601, IEC 62353 standards
c. Battery backup – see Unknown issues section. Must have 20 minutes back up battery in case of mains electricity failure.
d. Optionally hot swappable batteries so that it can be run on battery supply for an extended period, e.g. 2 hours for within hospital transfer.
e. Must avoid harmful RF or EM emissions that could interfere with other critical machinery.
3. Gas supply to patient.
a. User must be able to control inspired oxygen proportion (FiO2). The percentage of oxygen in the gas being breathed in by the patient. Room air is 21% oxygen.
b. At least (50% or 60%) and 100% options
c. Ideally variable between 30 – 100 % in 10% steps.

d. Patient breathing system connections: the ventilator must present 22mm outside diameter (OD) ‘male’ standard connectors to ISO 5356-1:2015 on both outlet and inlet ports for connection to user supplied 22mm ‘female’ connectors on the breathing system. These must be rigid and robust (not plastic) and separated by a minimum of 10 cm between centres to accommodate filter HMEs.
4. All elements in the gas pathway must meet biological safety and low-pressure oxygen safety standards, especially to minimise risk of fire or contamination of the patient’s airway.

Infection control
1. All parts coming into contact with the patient’s breath must be either disposable or able to be decontaminated between patients.
2. All external surfaces must be cleanable in the likely event that they get respiratory secretions or blood splatter on them. Cleaning would be by healthcare workers manually wiping using an approved surface wipe with disinfectant or cloths and approved surface cleaning liquid.
3. There will be a separately sourced HMEF-bacterial-viral filter between the machine and patient which may impact on resistance within the system, which may need to be accounted for with some designs. The pressure being delivered to the patient is the specified pressure. If the filter has a resistance of, say 2 cmH2O at 30 lpm, the ventilator needs to output 37 cmH2O to achieve a set 35 cmH2O at the patient. This will need further detailed consideration. Viral filtering filters may have much higher resistance that may be clinically relevant.
4. Optionally include facility for hot water humidifier to be included in breathing system.

Monitoring and Alarms
1. Must alarm at:
a. Gas or electricity supply failure.
b. Machine switched off while in mandatory ventilation mode.
c. Inspiratory airway pressure exceeded.
d. Inspiratory and PEEP pressure not achieved (equivalent to disconnection alarm).
e. Tidal volume not achieved or exceeded.
2. Monitoring – the following should be continuously displayed so the user can verify.

a. Current settings of tidal volume, frequency, PEEP, FiO2, ventilation mode.
b. Actual achieved rates of tidal volume, breathing rate, PEEP, plateau pressure, FiO2.
c. If it exists, in pressure support mode there must be real time confirmation of each patient breath and an alarm if below acceptable range.
d. Optionally CO2 monitoring included.

Miscellaneous
1. Must be reliable. It must have 100% duty cycle for up to 14 days.
2. Optionally it can be used beyond 14 days, the expected durability must be specified.
3. Can be floor standing.
4. Ideally small and light enough to mount on patient bed and orientation independent functioning.
5. Should be as robust as possible. For example, it may be dropped from bed height to floor.
6. It must be intuitive to use for qualified medical personnel, but these may not be specialists in ventilator use.
a. Must not require more than 30 minutes training for a doctor with some experience of ventilator use.
b. Must include Instructions for Use.
c. Ideally instructions for use should be built into the labelling of the ventilator, e.g. with ‘connect this to wall’ etc.
d. Must include clear labelling of all critical functions and controls using standard terms, pictograms and colours that will be readily recognised by UK healthcare staff.
7. Must have transparent design, supply chain, manufacture, quality assurance and testing processes that are of sufficient quality to enable MHRA officials to deem appropriate for usage in exceptional circumstances.
8. Must not be excessively cumbersome so that it would impede hospital operations or prevent easy movement within hospital premises.
9. Must be made from materials and parts readily available in the UK supply chain (anticipating increasing global restrictions on freight movement).
10. Standards – there are many standards that exist in this area. Below is a list of the most relevant ones. They are not formal regulatory requirements, but many are harmonised against regulatory requirements. Consider them as helpful advisory standards for now. MHRA will lead an exercise to define which can be ‘safely’ relaxed for this emergency situation.
a. BS EN 794-3:1998 +A2:2009 Particular requirements for emergency and transport ventilators
b. ISO 10651-3:1997 Lung Ventilators for Medical Use - Emergency and Transport
c. BS ISO 80601-2-84:2018 Medical electrical equipment. Part 2-84. Particular requirements for basic safety and essential performance of emergency and transport ventilators – especially the parts on ‘patient gas pathway’ safety (very similar to IEC 60601)
d. ISO 80601-2-12:2020 Medical electrical equipment — Part 2-12: Particular requirements for basic safety and essential performance of critical care ventilators
e. BS ISO 19223:2019 Lung ventilators and related equipment. Vocabulary and semantics

Testing
1. It is accepted that full demonstration of compliance to ISO 80601-2-12:2020 is unrealistic in the time frame required for development. Nevertheless, compliance with the essential safety standards must be demonstrated for patient safety.
2. It is not anticipated that devices will be CE marked and approval by the MHRA will be through the “Exceptional use of non-CE marked medical devices” route.
3. When the current emergency has passed these devices will NOT be usable for routine care unless they have been CE marked through the Medical Device Regulations. The device must display a prominent indelible label to this effect.
4. Usability testing at both prototype and final production stages will be required. This should be done as a short Formative Usability Test to ISO62366 (this can be done in a day) in a realistic environment if possible. The user will be wearing complex protective clothing which includes: Eye goggles (in addition to spectacles if worn), Face shield, Plastic apron, Surgical gown, Two layers of gloves, usually nitrile non-handed small, medium, large variants, Gloves are donned in layers and sticky taped onto sleeves of gown in between layers
5. The user must be able to instantly see the settings selected and be able to easily operate all controls while dressed in protective gear. They may be required to remain so clothed and operating the ventilator for a number of hours without breaks.

Unknown Issues
1. How plentiful is 4 bar oxygen supply?
a. Absolute minimum oxygen requirement is the human consumption of about 250 ml/min in a healthy person but upto 500 ml/min in severe sepsis. However, achieving this is only possible if certain breathing system designs are used and ‘driving’ gas is done by air.
i. Specifically, would have to use circle breathing system with active CO2 absorption. Is sufficient soda lime available?
b. If consumption in the range 1-2 l/min is acceptable then a wider range of designs is possible, but some very basic designs are not.
c. If consumption in the range 10l/min is acceptable then any possible design can be considered.
2. What is the resistance of HMEF-bacterial-viral filters that are to be used with the ventilator? Is it clinically relevant?
3. Is there any need to consider running from only low-pressure oxygen e.g. from a concentrator? This makes design more complex.
4. How plentiful is the supply of syringe drivers and drugs for sedation?
a. If limited, then a vaporiser could be used to vaporise Isoflurane for sedation.
b. This would need certain breathing system designs, mandatory AGSS and a supply of vaporisers.
5. If monitoring can be done by another machine it could be left out of the ventilator, but essential parameters must be available to the clinician.
6. Battery backup – Every current ventilator used inside hospitals has a battery backup, so users will expect it to be there and will behave as if it is, e.g. unplug it from the wall in order to rearrange cables or while manoeuvring the patient. However, this needs very careful thought to balance the risks. Including this in the spec means instantly trying to source 30,000 large, heavy batteries. Specifying a DC voltage (ie 12VDC) may well be the most sensible for the machine working voltage. Need the advice of an electronic engineer with military/resource limited experience before specifying anything here. It needs to be got right first time.

Glossary
ARDS – Acute Respiratory Distress Syndrome: a life-threatening form of respiratory failure where the lungs become severely inflamed due to an infection or injury and can't provide the body's vital organs with enough oxygen.

SIMV-PC – Synchronized Intermittent Mandatory Ventilation – Pressure Controlled: a mode of ventilation where the patient is allowed to take spontaneous breaths, the machine will assist the patients breathing when a spontaneous breath is taken. If the patient does not make a pre-set number of breaths a minute (i.e. 10) the machine provides mechanical ventilation to provide the set number.

PRVC – Pressure Regulated Volume Controlled: A mode of ventilation where a set tidal volume is delivered to the patient while maintain the lowest pressure possible in the airway, to avoid trauma.
BIPAP – Bilevel Positive Airway Pressure: a non-invasive ventilation mode that provides different levels of pressure when the patient inhales and exhales.
PEEP – Positive End-Expiratory Pressure: The lower pressure applied to the patient’s airway to allow them to breathe out, but not too much.
EPAP – Expiatory Positive Airway Pressure: Similar to PEEP, pressure applied to the airway on patient expiration to prevent collapse of the airway.
HMEF – Heat and Moisture Exchange Filter: device fitted to the patient end of the breathing system, contains hydrophobic medium that absorbs heat and moisture from the patients exhaled breath and uses absorbed moisture to humidify inhaled gases. Can also filter bacteria and viruses, this will be used on all patients. WARNING can affect delivered pressure.
RF – Radio Frequency: Many medical devices are sensitive to RF interference. Care should be taken to ensure that this is kept to a minimum.
EM – Electro Magnetic Emissions: Many medical devices are sensitive to EM interference. Care should be taken to ensure that this is kept to a minimum.
Fi02 – Fraction of inspired oxygen: concentration of oxygen in the gas mixture that the patient inhales
AGSS – Anaesthetic gas scavenging system: where anaesthetic agents have been included in the gas mixture, this system is used to collect and remove exhales gas to avoid exposure to health care professionals.

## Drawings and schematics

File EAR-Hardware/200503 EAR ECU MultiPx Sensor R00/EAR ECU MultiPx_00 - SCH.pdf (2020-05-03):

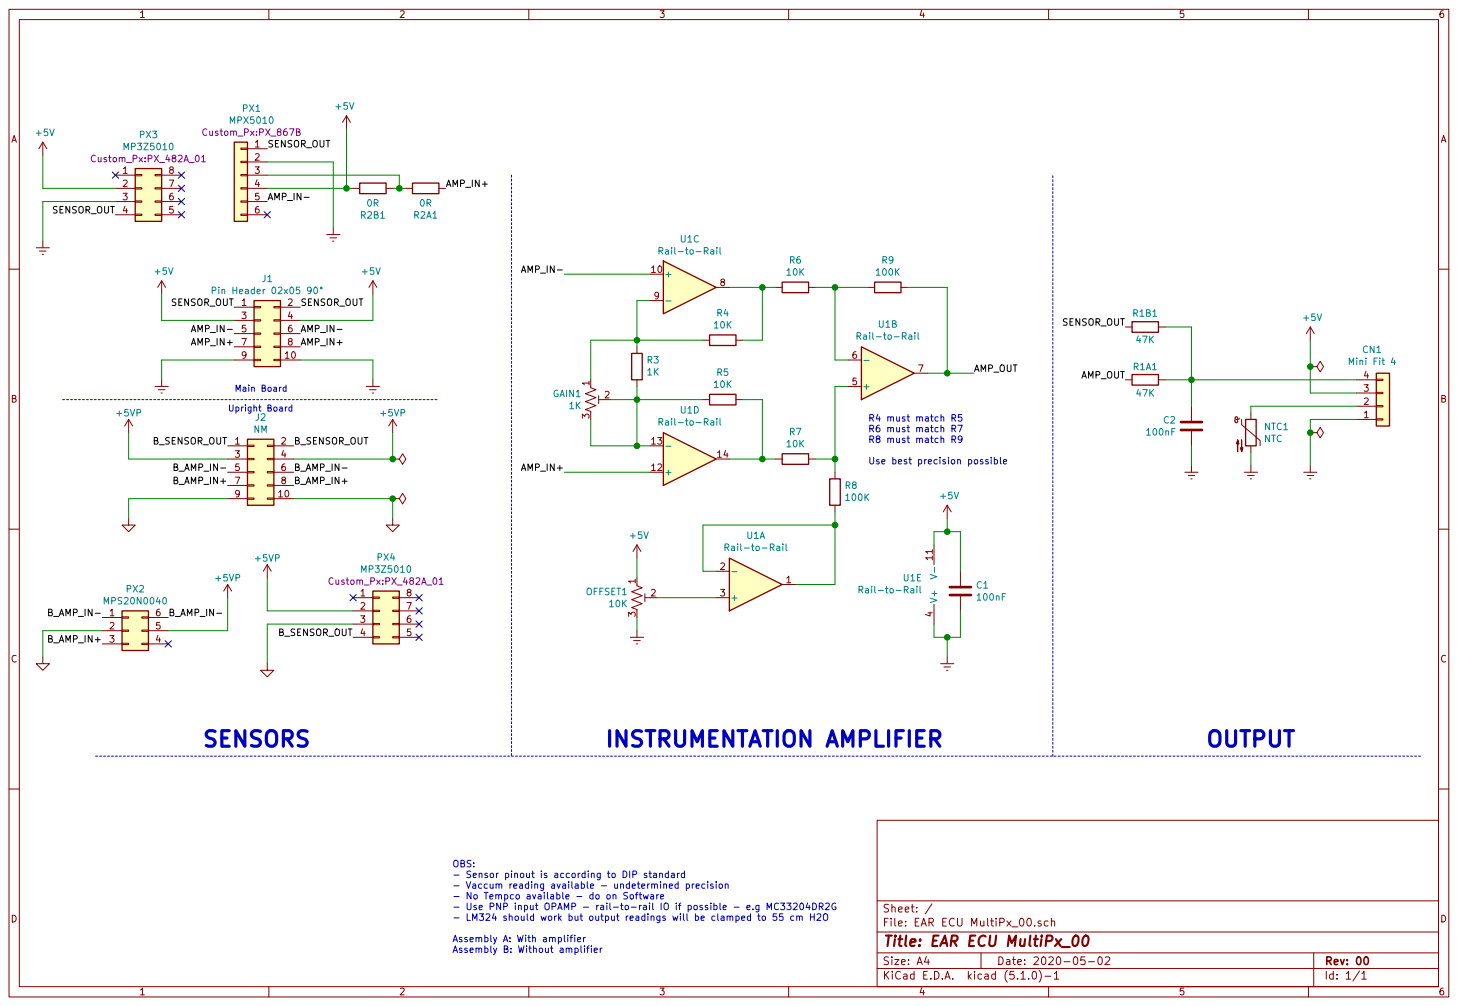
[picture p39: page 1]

Rail-to-Rail OBS: - Sensor pinout is according to DIP standard

- Vaccum reading available - undetermined precision
- No Tempco available - do on Software
- Use PNP input OPAMP - rail-to-rail IO if possible - e.g MC33204DR2G
- LM324 should work but output readings will be clamped to 55 cm H2O

File: EAR ECU MultiPx_00.sch Sheet: /
Id: 1/1 Title: EAR ECU MultiPx_00

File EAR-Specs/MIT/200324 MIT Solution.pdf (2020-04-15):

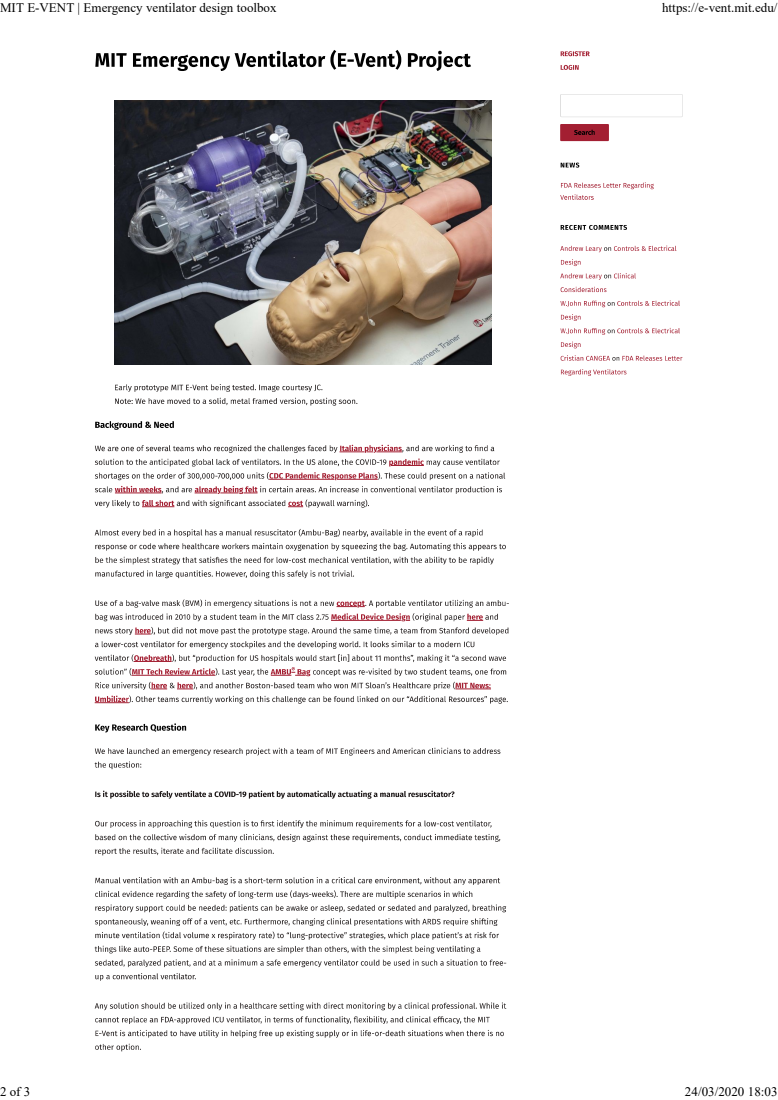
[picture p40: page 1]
MIT E-VENT | Emergency ventilator design toolbox; https://e-vent.mit.edu/

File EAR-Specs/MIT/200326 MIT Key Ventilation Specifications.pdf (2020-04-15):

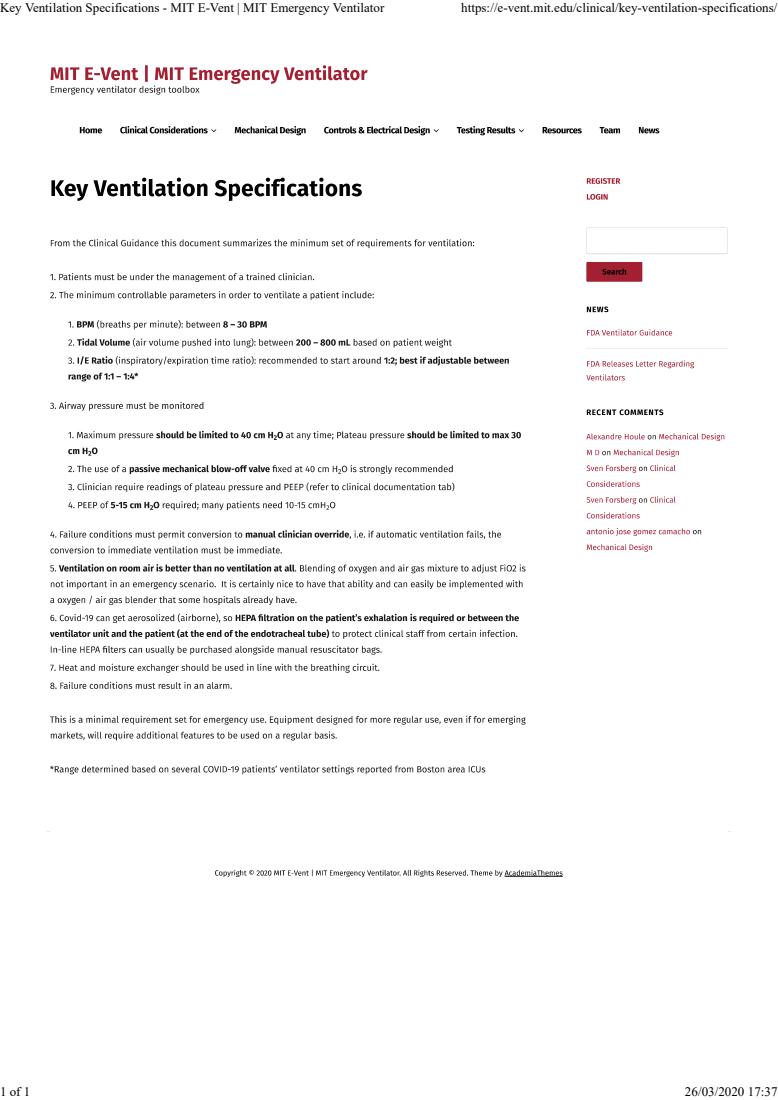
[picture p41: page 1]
Key Ventilation Specifications - MIT E-Vent | MIT Emergency Ventilator; https://e-vent.mit.edu/clinical/key-ventilation-specifications/

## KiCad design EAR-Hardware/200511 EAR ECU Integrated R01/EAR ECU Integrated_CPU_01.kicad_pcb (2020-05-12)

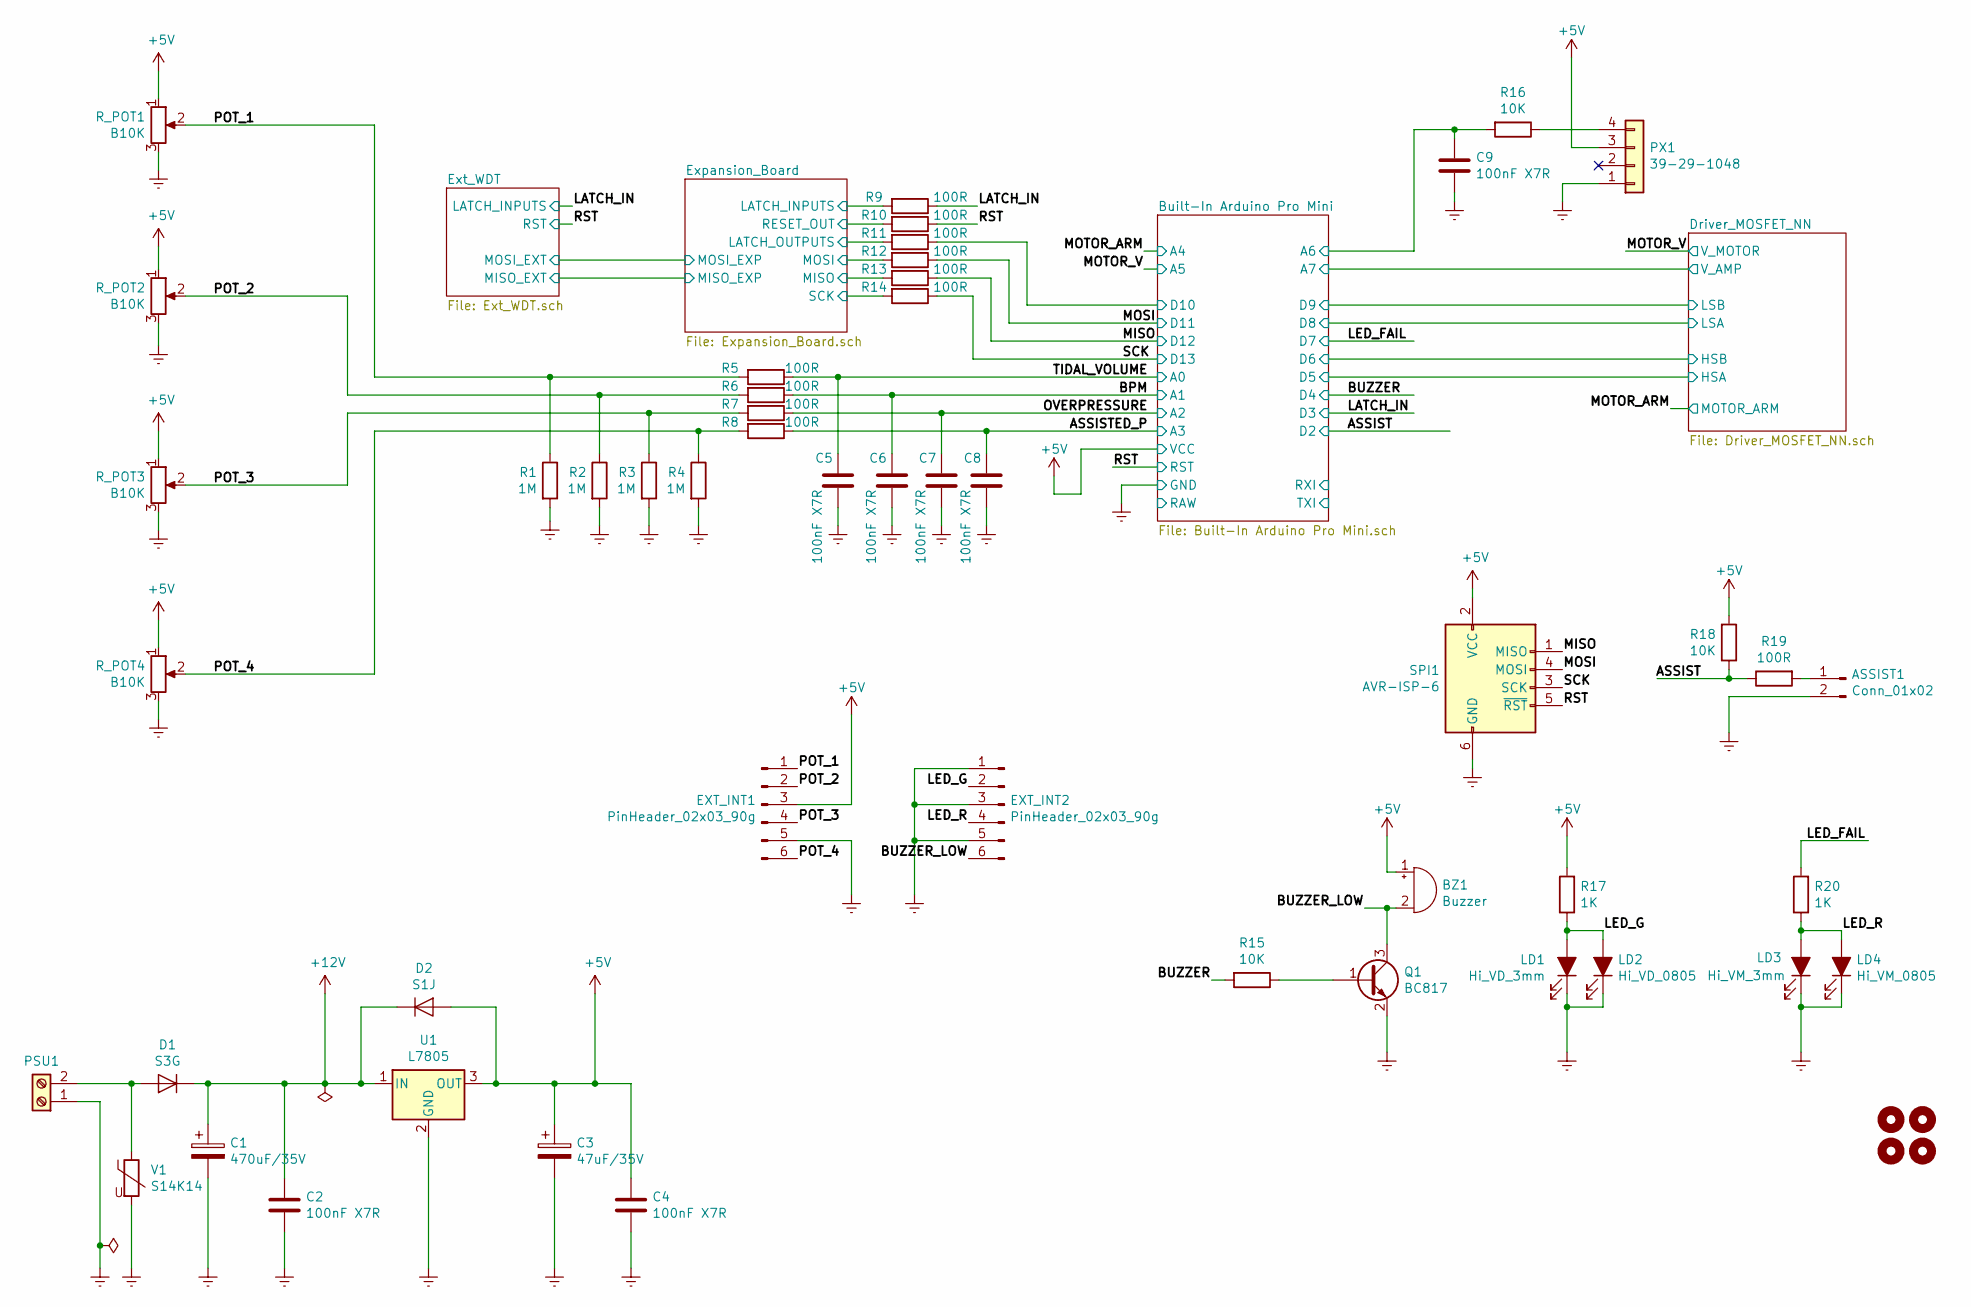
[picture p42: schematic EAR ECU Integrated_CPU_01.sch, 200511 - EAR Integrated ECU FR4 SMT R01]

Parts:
ASSIST1: Conn_01x02; SolderWirePad_1x02_P3.81mm_Drill1mm
BZ1: Buzzer; Buzzer_TDK_PS1240P02BT_D12.2mm_H6.5mm
C1: 470uF/35V; CP_Radial_D10.0mm_P5.00mm
C2, C4, C5, C6, C7, C8, C9: 100nF X7R; C_0805_2012Metric
C3: 47uF/35V; CP_Radial_D5.0mm_P2.50mm
D1: S3G; D_SMC
D2: S1J; D_SMA
EXT_INT1, EXT_INT2: PinHeader_02x03_90g; PinHeader_2x03_P2.54mm_Horizontal
H1, H2, H3, H4: MountingHole; MountingHole_3.5mm_Pad_Via
LD1: Hi_VD_3mm; LED_D3.0mm_Clear
LD2: Hi_VD_0805; LED_0805_2012Metric
LD3: Hi_VM_3mm; LED_D3.0mm_Clear
LD4: Hi_VM_0805; LED_0805_2012Metric
PSU1: TerminalBlock_Phoenix:TerminalBlock_Phoenix_MKDS-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; TerminalBlock_Phoenix_MKDS-1,5-2-5.08_1x02_P5.08mm_Horizont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
PX1: 39-29-1048; MOLEX-39-29-1048
Q1: BC817; SOT-23
R1, R2, R3, R4: 1M; R_0805_2012Metric
R5, R6, R7, R8, R9, R10, R11, R12, R13, R14, R19: 100R; R_0805_2012Metric
R15, R16, R18: 10K; R_0805_2012Metric
R17, R20: 1K; R_0805_2012Metric
R_POT1, R_POT2, R_POT3, R_POT4: B10K; PDB18_Series_Bourns
SPI1: AVR-ISP-6; PinHeader_2x03_P2.54mm_Vertical
U1: L7805; TO-263-3_Hybrid_TO-220_Tab_Dw
V1: S14K14; RV_Disc_D12mm_W3.9mm_P7.5mm

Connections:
+5V: BZ1.1 (-), C3.1, C4.1, D2.2 (A), EXT_INT1.3, PX1.3, R17.2, R18.2, R_POT1.1, R_POT2.1, R_POT3.1, R_POT4.1, SPI1.2 (VCC), U1.3 (OUT); also elsewhere on the board
+12V: C1.1, C2.1, D1.1 (K), D2.1 (K), U1.1 (IN); also elsewhere on the board
/ASSIST: R18.1, R19.1; also elsewhere on the board
/ASSISTED_P: C8.1, R8.1; also elsewhere on the board
/BPM: C6.1, R6.1; also elsewhere on the board
/BUZZER: R15.2; also elsewhere on the board
/BUZZER_LOW: BZ1.2 (+), EXT_INT2.6, Q1.3 (C)
/Built-In Arduino Pro Mini/A6: C9.1, R16.2; also elsewhere on the board
/Built-In Arduino Pro Mini/D10: R11.1; also elsewhere on the board
/Expansion_Board/LATCH_INPUTS: R9.2; also elsewhere on the board
/Expansion_Board/LATCH_OUTPUTS: R11.2; also elsewhere on the board
/Expansion_Board/MISO: R13.2; also elsewhere on the board
/Expansion_Board/MOSI: R12.2; also elsewhere on the board
/Expansion_Board/RESET_OUT: R10.2; also elsewhere on the board
/Expansion_Board/SCK: R14.2; also elsewhere on the board
/LATCH_IN: R9.1; also elsewhere on the board
/LED_FAIL: R20.2; also elsewhere on the board
/LED_G: EXT_INT2.2, LD1.2 (A), LD2.2 (A), R17.1
/LED_R: EXT_INT2.4, LD3.2 (A), LD4.2 (A), R20.1
/MISO: R13.1, SPI1.1 (MISO); also elsewhere on the board
/MOSI: R12.1, SPI1.4 (MOSI); also elsewhere on the board
/OVERPRESSURE: C7.1, R7.1; also elsewhere on the board
/POT_1: EXT_INT1.1, R1.1, R5.2, R_POT1.2
/POT_2: EXT_INT1.2, R2.1, R6.2, R_POT2.2
/POT_3: EXT_INT1.4, R3.1, R7.2, R_POT3.2
/POT_4: EXT_INT1.6, R4.1, R8.2, R_POT4.2
/RST: R10.1, SPI1.5 (~RST); also elsewhere on the board
/SCK: R14.1, SPI1.3 (SCK); also elsewhere on the board
/TIDAL_VOLUME: C5.1, R5.1; also elsewhere on the board
unnamed: ASSIST1.1, R19.2
unnamed: D1.2 (A), PSU1.2, V1.1
unnamed: PX1.4, R16.1
unnamed: Q1.1 (B), R15.1

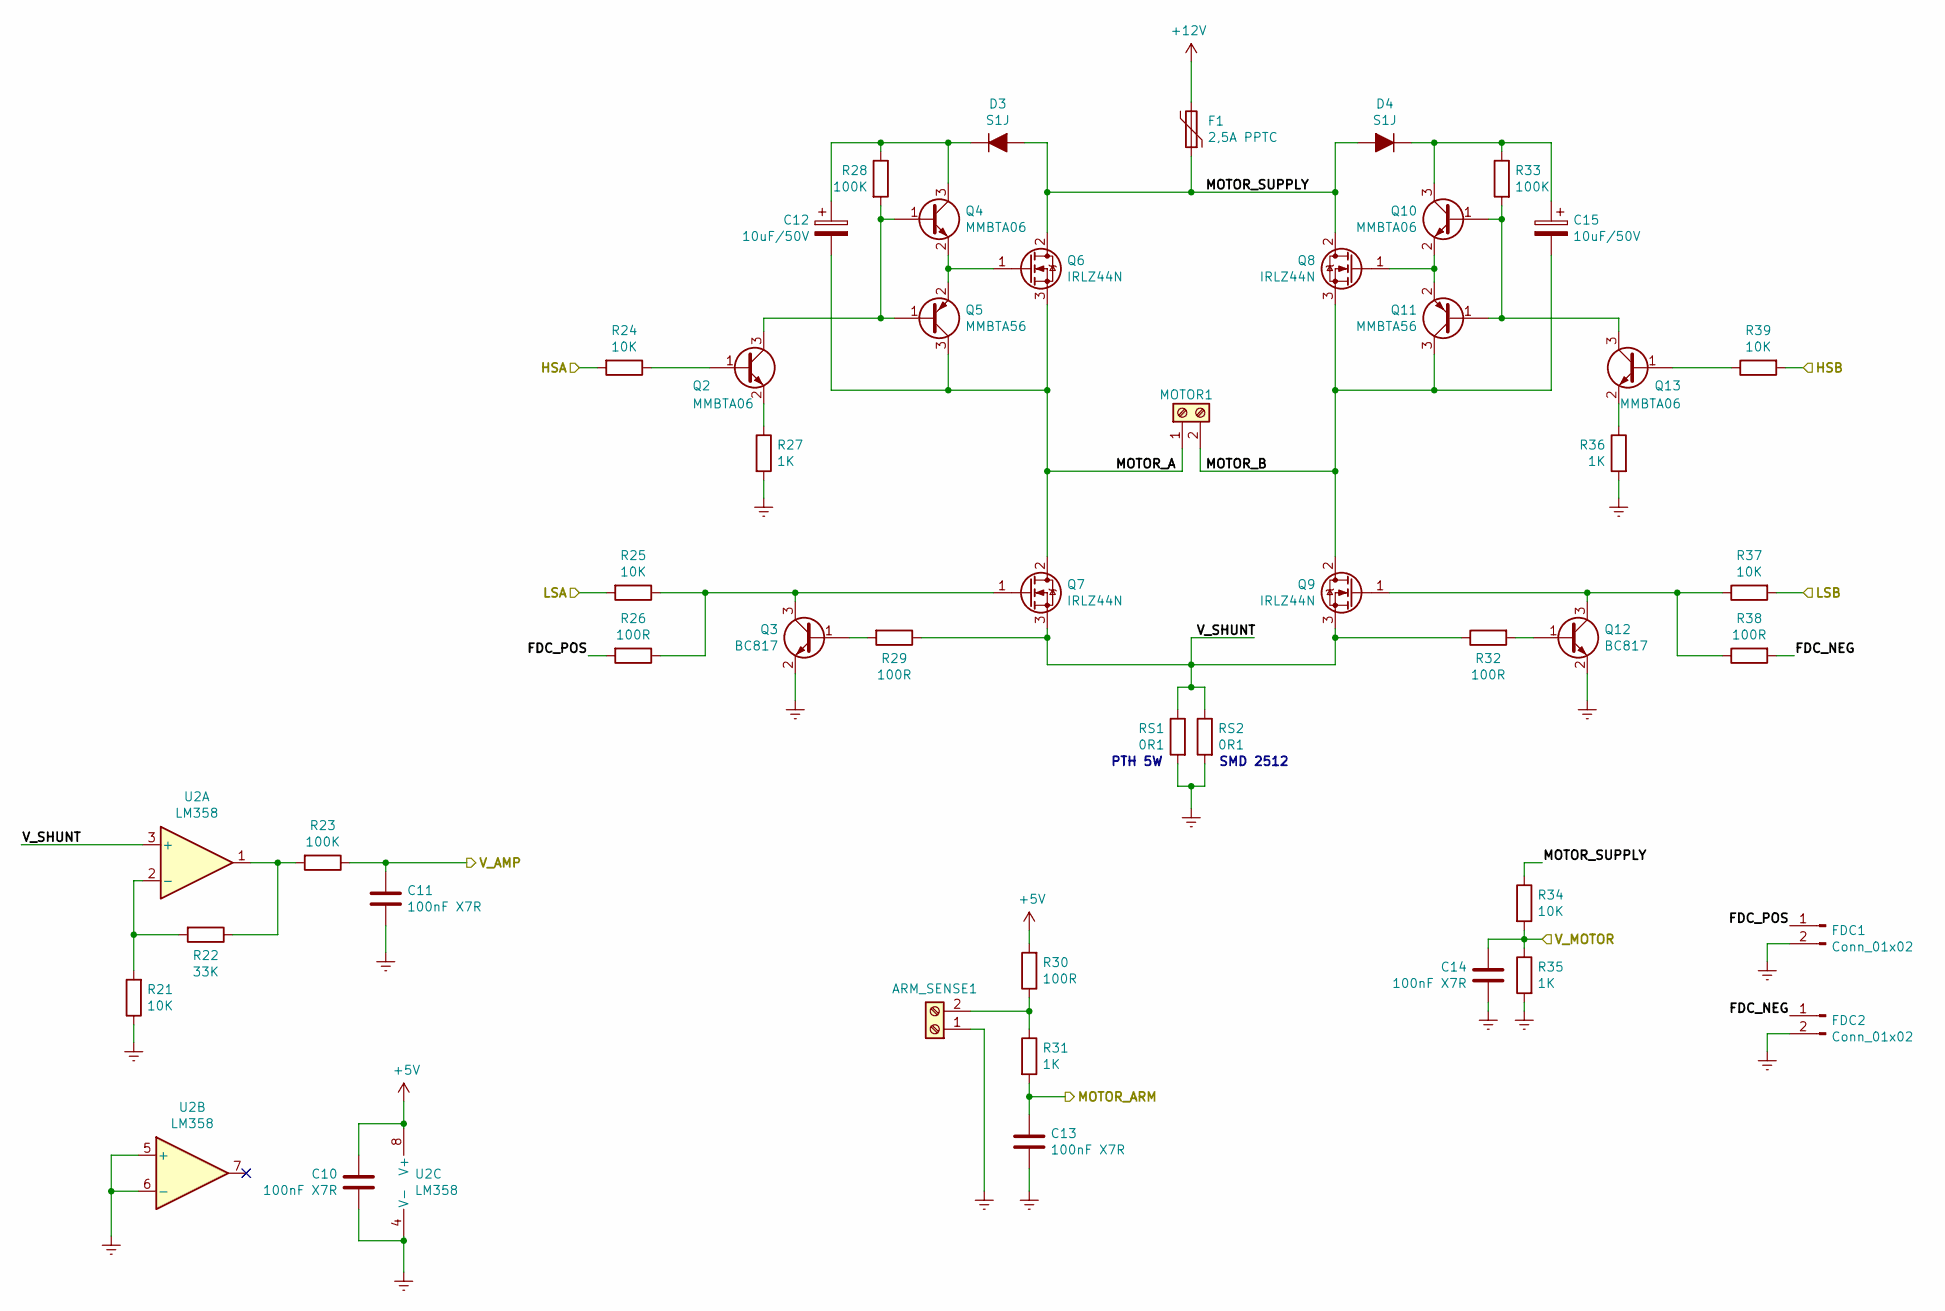
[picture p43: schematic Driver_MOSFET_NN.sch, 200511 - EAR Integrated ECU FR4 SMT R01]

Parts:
ARM_SENSE1: Screw_Terminal_01x02; TerminalBlock_Phoenix_MKDS-1,5-2-5.08_1x02_P5.08mm_Horizont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
C10, C11, C13, C14: 100nF X7R; C_0805_2012Metric
C12, C15: 10uF/50V; CP_Radial_D5.0mm_P2.50mm
D3, D4: S1J; D_SMA
F1: 2,5A PPTC; RV_Disc_D7mm_W3.4mm_P5mm
FDC1, FDC2: Conn_01x02; PinSocket_1x02_P2.54mm_Vertical
MOTOR1: Conn_01x02; TerminalBlock_Phoenix_MKDS-1,5-2-5.08_1x02_P5.08mm_Horizont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
Q2, Q4, Q10, Q13: MMBTA06; SOT-23
Q3, Q12: BC817; SOT-23
Q5, Q11: MMBTA56; SOT-23
Q6, Q7, Q8, Q9: IRLZ44N; TO-263-3_Hybrid_TO-220_Tab_Dw
R21, R24, R25, R34, R37, R39: 10K; R_0805_2012Metric
R22: 33K; R_0805_2012Metric
R23, R28, R33: 100K; R_0805_2012Metric
R26, R29, R30, R32, R38: 100R; R_0805_2012Metric
R27, R31, R35, R36: 1K; R_0805_2012Metric
RS1: 0R1; R_Axial_Power_L20.0mm_W6.4mm_P7.62mm_Vertical
RS2: 0R1; R_2512_6332Metric_Pad1.52x3.35mm_HandSolder
U2: LM358; SOIC-8_3.9x4.9mm_P1.27mm

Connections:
+5V: C10.1, R30.2, U2.8 (V+); also elsewhere on the board
+12V: F1.2; also elsewhere on the board
/Built-In Arduino Pro Mini/A7: C11.1, R23.1; also elsewhere on the board
/Built-In Arduino Pro Mini/D5: R24.2; also elsewhere on the board
/Built-In Arduino Pro Mini/D6: R39.2; also elsewhere on the board
/Built-In Arduino Pro Mini/D8: R25.2; also elsewhere on the board
/Built-In Arduino Pro Mini/D9: R37.2; also elsewhere on the board
/Driver_MOSFET_NN/FDC_NEG: FDC2.1, R38.2
/Driver_MOSFET_NN/FDC_POS: FDC1.1, R26.2
/Driver_MOSFET_NN/MOTOR_A: C12.2, MOTOR1.1, Q5.3 (C), Q6.3 (S), Q7.2 (D)
/Driver_MOSFET_NN/MOTOR_B: C15.2, MOTOR1.2, Q8.3 (S), Q9.2 (D), Q11.3 (C)
/Driver_MOSFET_NN/MOTOR_SUPPLY: D3.2 (A), D4.2 (A), F1.1, Q6.2 (D), Q8.2 (D), R34.1
/Driver_MOSFET_NN/Q6G: Q4.2 (E), Q5.2 (E), Q6.1 (G)
/Driver_MOSFET_NN/Q7G: Q3.3 (C), Q7.1 (G), R25.1, R26.1
/Driver_MOSFET_NN/Q8G: Q8.1 (G), Q10.2 (E), Q11.2 (E)
/Driver_MOSFET_NN/Q9G: Q9.1 (G), Q12.3 (C), R37.1, R38.1
/Driver_MOSFET_NN/V_SHUNT: Q7.3 (S), Q9.3 (S), R29.1, R32.1, RS1.1, RS2.1, U2.3 (+)
/MOTOR_ARM: C13.1, R31.2; also elsewhere on the board
/MOTOR_V: C14.1, R34.2, R35.1; also elsewhere on the board
unnamed: ARM_SENSE1.2, R30.1, R31.1
unnamed: C12.1, D3.1 (K), Q4.3 (C), R28.1
unnamed: C15.1, D4.1 (K), Q10.3 (C), R33.1
unnamed: Q2.1 (B), R24.1
unnamed: Q2.2 (E), R27.1
unnamed: Q2.3 (C), Q4.1 (B), Q5.1 (B), R28.2
unnamed: Q3.1 (B), R29.2
unnamed: Q10.1 (B), Q11.1 (B), Q13.3 (C), R33.2
unnamed: Q12.1 (B), R32.2
unnamed: Q13.1 (B), R39.1
unnamed: Q13.2 (E), R36.1
unnamed: R21.2, R22.2, U2.2 (-)
unnamed: R22.1, R23.2, U2.1

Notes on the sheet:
PTH 5W
SMD 2512

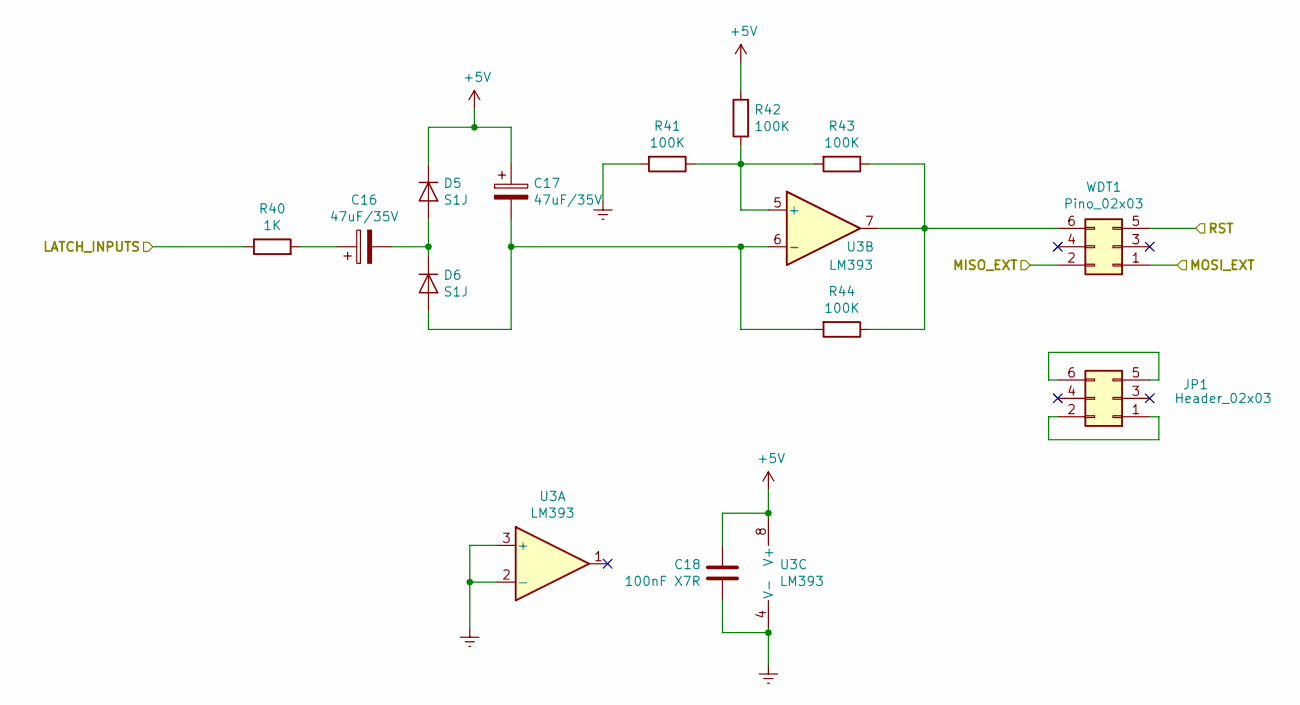
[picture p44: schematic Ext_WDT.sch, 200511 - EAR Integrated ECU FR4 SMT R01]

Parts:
C16, C17: 47uF/35V; CP_Radial_D5.0mm_P2.50mm
C18: 100nF X7R; C_0805_2012Metric
D5, D6: S1J; D_SMA
JP1: Header_02x03; PinSocket_2x03_P2.54mm_Vertical
R40: 1K; R_0805_2012Metric
R41, R42, R43, R44: 100K; R_0805_2012Metric
U3: LM393; SOIC-8_3.9x4.9mm_P1.27mm
WDT1: Pino_02x03; PinHeader_2x03_P2.54mm_Vertical

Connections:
+5V: C17.1, C18.1, D5.1 (K), R42.2, U3.8 (V+); also elsewhere on the board
/Expansion_Board/MISO_EXP: WDT1.2; also elsewhere on the board
/Expansion_Board/MOSI_EXP: WDT1.1; also elsewhere on the board
/LATCH_IN: R40.1; also elsewhere on the board
/RST: WDT1.5; also elsewhere on the board
unnamed: C16.1, R40.2
unnamed: C16.2, D5.2 (A), D6.1 (K)
unnamed: C17.2, D6.2 (A), R44.2, U3.6 (-)
unnamed: JP1.1, JP1.2
unnamed: JP1.5, JP1.6
unnamed: R41.1, R42.1, R43.2, U3.5 (+)
unnamed: R43.1, R44.1, U3.7, WDT1.6

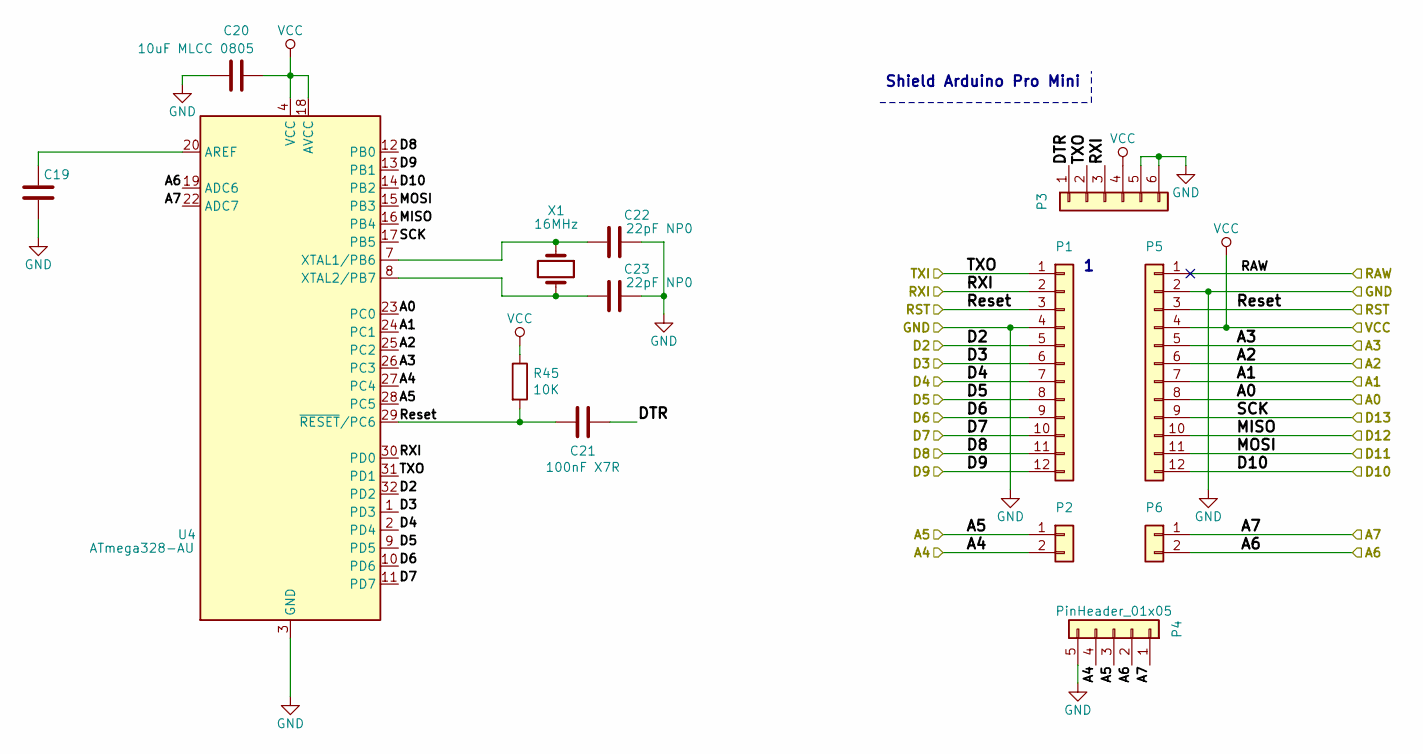
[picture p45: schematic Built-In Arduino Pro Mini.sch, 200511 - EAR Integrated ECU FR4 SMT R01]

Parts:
C19, C21: 100nF X7R; C_0805_2012Metric
C20: 10uF MLCC 0805; C_0805_2012Metric
C22, C23: 22pF NP0; C_0805_2012Metric
P1, P5: PinHeader_01x12; PinHeader_1x12_P2.54mm_Vertical
P2, P6: PinHeader_01x02; PinHeader_1x02_P2.54mm_Vertical
P3: PinHeader_01x06; PinHeader_1x06_P2.54mm_Vertical
P4: PinHeader_01x05; PinHeader_1x05_P2.54mm_Vertical
R45: 10K; R_0805_2012Metric
U4: ATmega328-AU; TQFP-32_7x7mm_P0.8mm
X1: 16MHz; Crystal_HC49-4H_Vertical

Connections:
+5V: C20.2, P3.4, P5.4, R45.1, U4.4 (VCC), U4.6 (VCC), U4.18 (AVCC); also elsewhere on the board
/ASSIST: P1.5, U4.32 (PD2); also elsewhere on the board
/ASSISTED_P: P5.5, U4.26 (PC3); also elsewhere on the board
/BPM: P5.7, U4.24 (PC1); also elsewhere on the board
/BUZZER: P1.7, U4.2 (PD4); also elsewhere on the board
/Built-In Arduino Pro Mini/A6: P4.2, P6.2, U4.19 (ADC6); also elsewhere on the board
/Built-In Arduino Pro Mini/A7: P4.1, P6.1, U4.22 (ADC7); also elsewhere on the board
/Built-In Arduino Pro Mini/D5: P1.8, U4.9 (PD5); also elsewhere on the board
/Built-In Arduino Pro Mini/D6: P1.9, U4.10 (PD6); also elsewhere on the board
/Built-In Arduino Pro Mini/D8: P1.11, U4.12 (PB0); also elsewhere on the board
/Built-In Arduino Pro Mini/D9: P1.12, U4.13 (PB1); also elsewhere on the board
/Built-In Arduino Pro Mini/D10: P5.12, U4.14 (PB2); also elsewhere on the board
/Built-In Arduino Pro Mini/DTR: C21.2, P3.1
/Built-In Arduino Pro Mini/RAW: P5.1
/Built-In Arduino Pro Mini/RXI: P1.2, P3.3, U4.30 (PD0)
/Built-In Arduino Pro Mini/TXI: P1.1, P3.2, U4.31 (PD1)
/LATCH_IN: P1.6, U4.1 (PD3); also elsewhere on the board
/LED_FAIL: P1.10, U4.11 (PD7); also elsewhere on the board
/MISO: P5.10, U4.16 (PB4); also elsewhere on the board
/MOSI: P5.11, U4.15 (PB3); also elsewhere on the board
/MOTOR_ARM: P2.2, P4.4, U4.27 (PC4); also elsewhere on the board
/MOTOR_V: P2.1, P4.3, U4.28 (PC5); also elsewhere on the board
/OVERPRESSURE: P5.6, U4.25 (PC2); also elsewhere on the board
/RST: C21.1, P1.3, P5.3, R45.2, U4.29 (~RESET~/PC6); also elsewhere on the board
/SCK: P5.9, U4.17 (PB5); also elsewhere on the board
/TIDAL_VOLUME: P5.8, U4.23 (PC0); also elsewhere on the board
unnamed: C19.1, U4.20 (AREF)
unnamed: C22.1, U4.7 (XTAL1/PB6), X1.1
unnamed: C23.1, U4.8 (XTAL2/PB7), X1.2

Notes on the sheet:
Shield Arduino Pro Mini

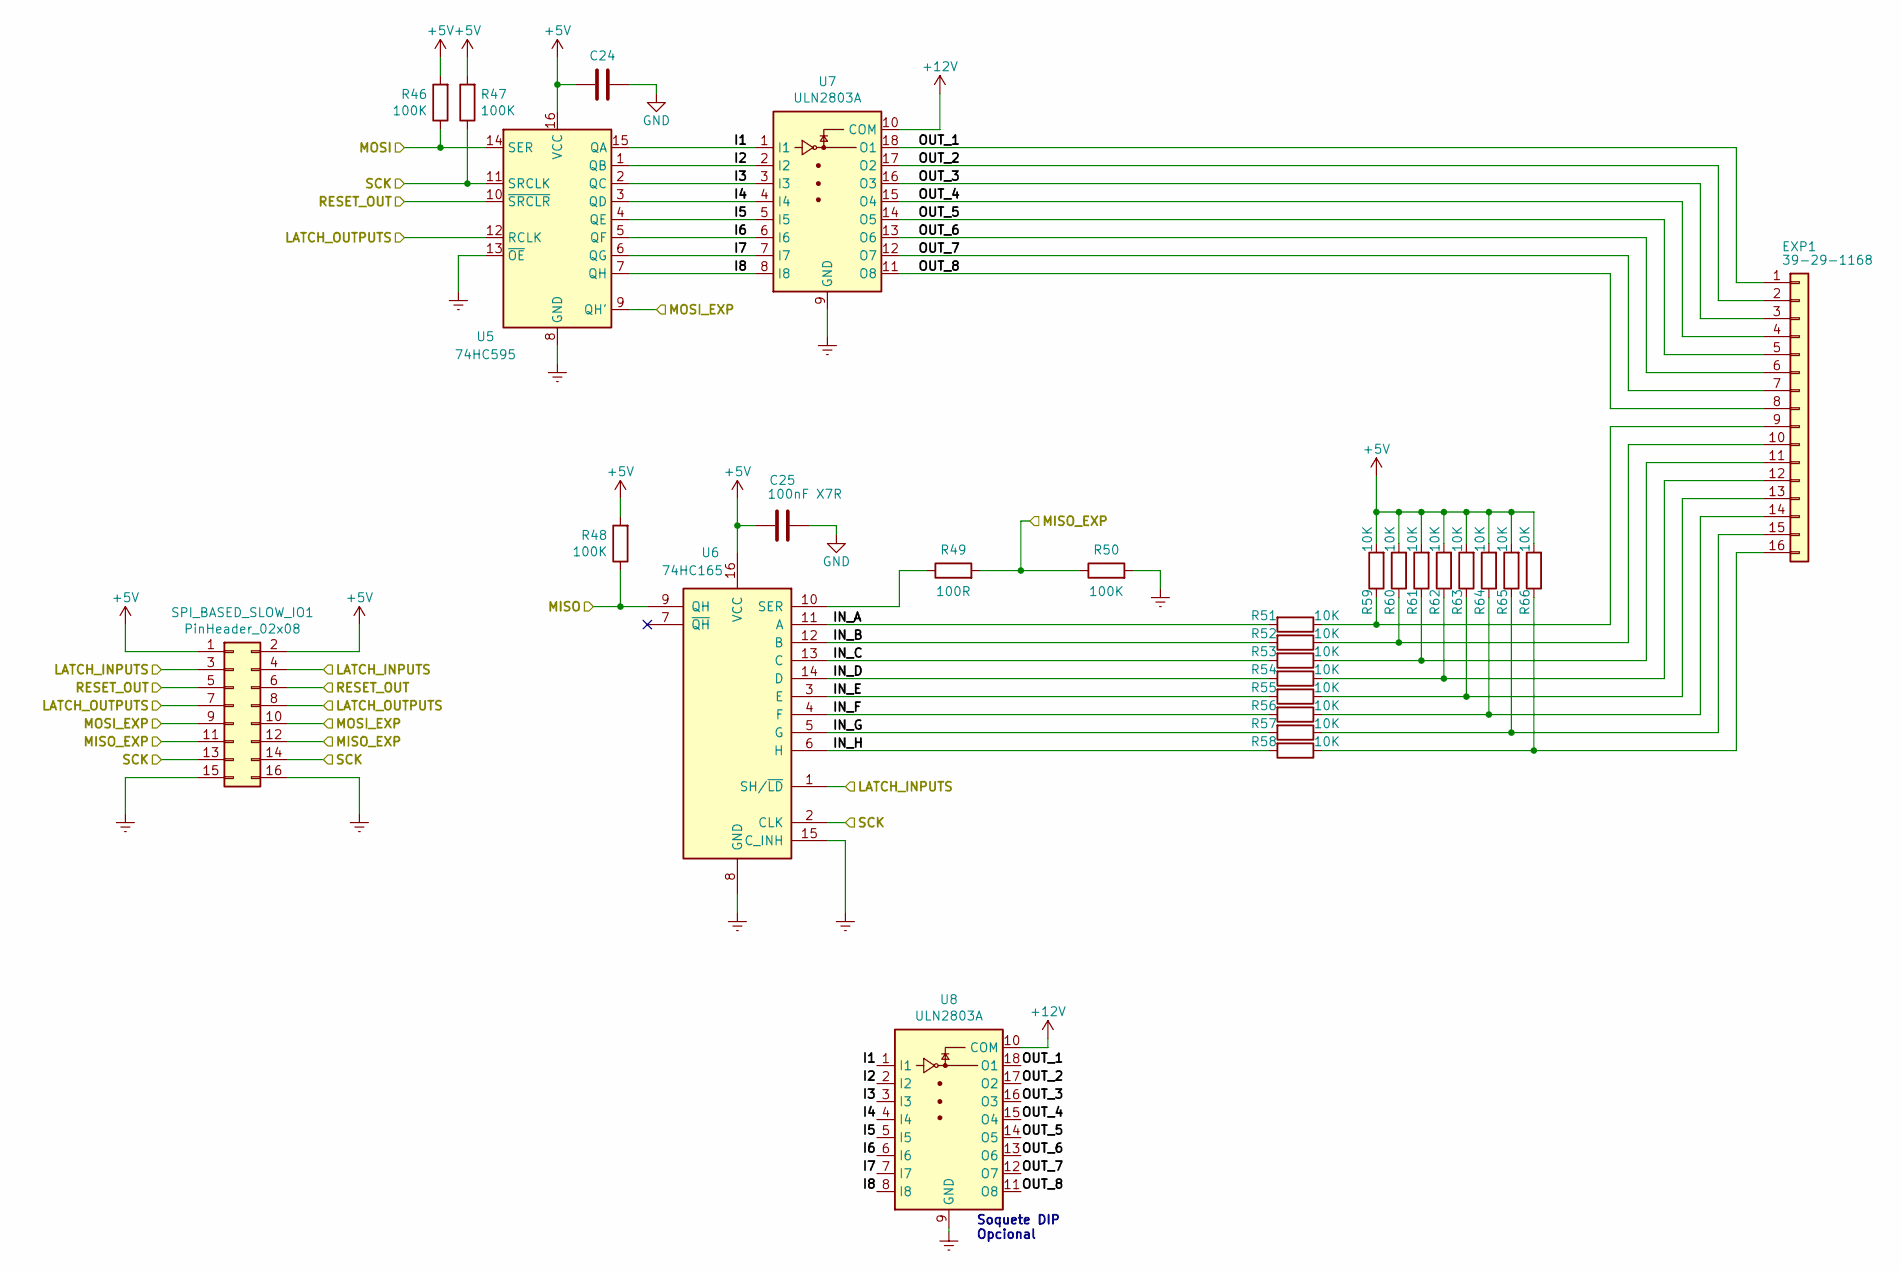
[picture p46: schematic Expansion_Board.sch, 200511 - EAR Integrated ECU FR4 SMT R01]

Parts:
C24, C25: 100nF X7R; C_0805_2012Metric
EXP1: 39-29-1168; MOLEX-39-29-1168
R46, R47, R48, R50: 100K; R_0805_2012Metric
R49: 100R; R_0805_2012Metric
R51, R52, R53, R54, R55, R56, R57, R58, R59, R60, R61, R62, R63, R64, R65, R66: 10K; R_0805_2012Metric
SPI_BASED_SLOW_IO1: PinHeader_02x08; PinHeader_2x08_P2.54mm_Vertical
U5: 74HC595; SOIC-16_3.9x9.9mm_P1.27mm
U6: 74HC165; SOIC-16_3.9x9.9mm_P1.27mm
U7: ULN2803A; SOIC-18W_7.5x11.6mm_P1.27mm
U8: ULN2803A; DIP-18_W7.62mm

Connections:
+5V: C24.2, C25.2, R46.2, R47.2, R48.2, R59.2, R60.2, R61.2, R62.2, R63.2, R64.2, R65.2, R66.2, SPI_BASED_SLOW_IO1.1, SPI_BASED_SLOW_IO1.2, U5.16 (VCC), U6.16 (VCC); also elsewhere on the board
+12V: U7.10 (COM), U8.10 (COM); also elsewhere on the board
/Expansion_Board/I1: U5.15 (QA), U7.1 (I1), U8.1 (I1)
/Expansion_Board/I2: U5.1 (QB), U7.2 (I2), U8.2 (I2)
/Expansion_Board/I3: U5.2 (QC), U7.3 (I3), U8.3 (I3)
/Expansion_Board/I4: U5.3 (QD), U7.4 (I4), U8.4 (I4)
/Expansion_Board/I5: U5.4 (QE), U7.5 (I5), U8.5 (I5)
/Expansion_Board/I6: U5.5 (QF), U7.6 (I6), U8.6 (I6)
/Expansion_Board/I7: U5.6 (QG), U7.7 (I7), U8.7 (I7)
/Expansion_Board/I8: U5.7 (QH), U7.8 (I8), U8.8 (I8)
/Expansion_Board/IN_A: R51.2, U6.11 (A)
/Expansion_Board/IN_B: R52.2, U6.12 (B)
/Expansion_Board/IN_C: R53.2, U6.13 (C)
/Expansion_Board/IN_D: R54.2, U6.14 (D)
/Expansion_Board/IN_E: R55.2, U6.3 (E)
/Expansion_Board/IN_F: R56.2, U6.4 (F)
/Expansion_Board/IN_G: R57.2, U6.5 (G)
/Expansion_Board/IN_H: R58.2, U6.6 (H)
/Expansion_Board/LATCH_INPUTS: SPI_BASED_SLOW_IO1.3, SPI_BASED_SLOW_IO1.4, U6.1 (SH/~LD); also elsewhere on the board
/Expansion_Board/LATCH_OUTPUTS: SPI_BASED_SLOW_IO1.7, SPI_BASED_SLOW_IO1.8, U5.12 (RCLK); also elsewhere on the board
/Expansion_Board/MISO: R48.1, U6.9 (QH); also elsewhere on the board
/Expansion_Board/MISO_EXP: R49.2, R50.1, SPI_BASED_SLOW_IO1.11, SPI_BASED_SLOW_IO1.12; also elsewhere on the board
/Expansion_Board/MOSI: R46.1, U5.14 (SER); also elsewhere on the board
/Expansion_Board/MOSI_EXP: SPI_BASED_SLOW_IO1.9, SPI_BASED_SLOW_IO1.10, U5.9 (QH'); also elsewhere on the board
/Expansion_Board/OUT_1: EXP1.1, U7.18 (O1), U8.18 (O1)
/Expansion_Board/OUT_2: EXP1.2, U7.17 (O2), U8.17 (O2)
/Expansion_Board/OUT_3: EXP1.3, U7.16 (O3), U8.16 (O3)
/Expansion_Board/OUT_4: EXP1.4, U7.15 (O4), U8.15 (O4)
/Expansion_Board/OUT_5: EXP1.5, U7.14 (O5), U8.14 (O5)
/Expansion_Board/OUT_6: EXP1.6, U7.13 (O6), U8.13 (O6)
/Expansion_Board/OUT_7: EXP1.7, U7.12 (O7), U8.12 (O7)
/Expansion_Board/OUT_8: EXP1.8, U7.11 (O8), U8.11 (O8)
/Expansion_Board/RESET_OUT: SPI_BASED_SLOW_IO1.5, SPI_BASED_SLOW_IO1.6, U5.10 (~SRCLR); also elsewhere on the board
/Expansion_Board/SCK: R47.1, SPI_BASED_SLOW_IO1.13, SPI_BASED_SLOW_IO1.14, U5.11 (SRCLK), U6.2 (CLK); also elsewhere on the board
unnamed: EXP1.9, R51.1, R59.1
unnamed: EXP1.10, R52.1, R60.1
unnamed: EXP1.11, R53.1, R61.1
unnamed: EXP1.12, R54.1, R62.1
unnamed: EXP1.13, R55.1, R63.1
unnamed: EXP1.14, R56.1, R64.1
unnamed: EXP1.15, R57.1, R65.1
unnamed: EXP1.16, R58.1, R66.1
unnamed: R49.1, U6.10 (SER)

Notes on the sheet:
Soquete DIP Opcional

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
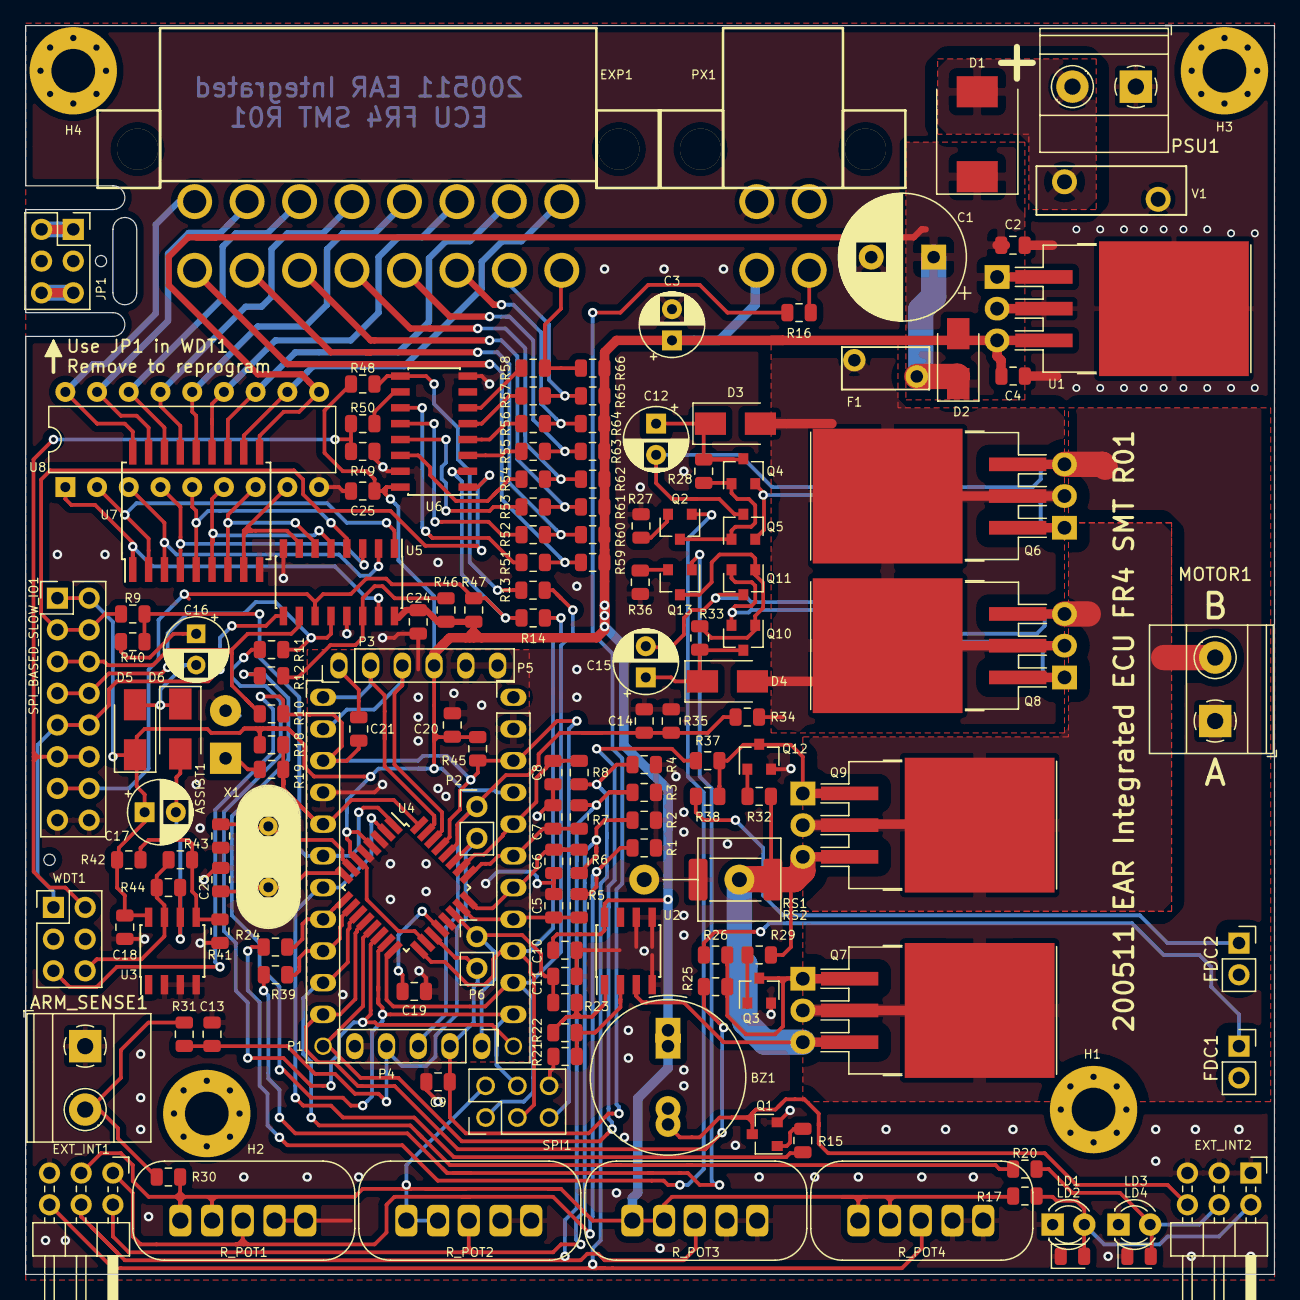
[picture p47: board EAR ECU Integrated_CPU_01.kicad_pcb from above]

Board: 2 copper layers, 100.0 x 100.0 mm, 156 parts (0 on the bottom side), 112 nets.

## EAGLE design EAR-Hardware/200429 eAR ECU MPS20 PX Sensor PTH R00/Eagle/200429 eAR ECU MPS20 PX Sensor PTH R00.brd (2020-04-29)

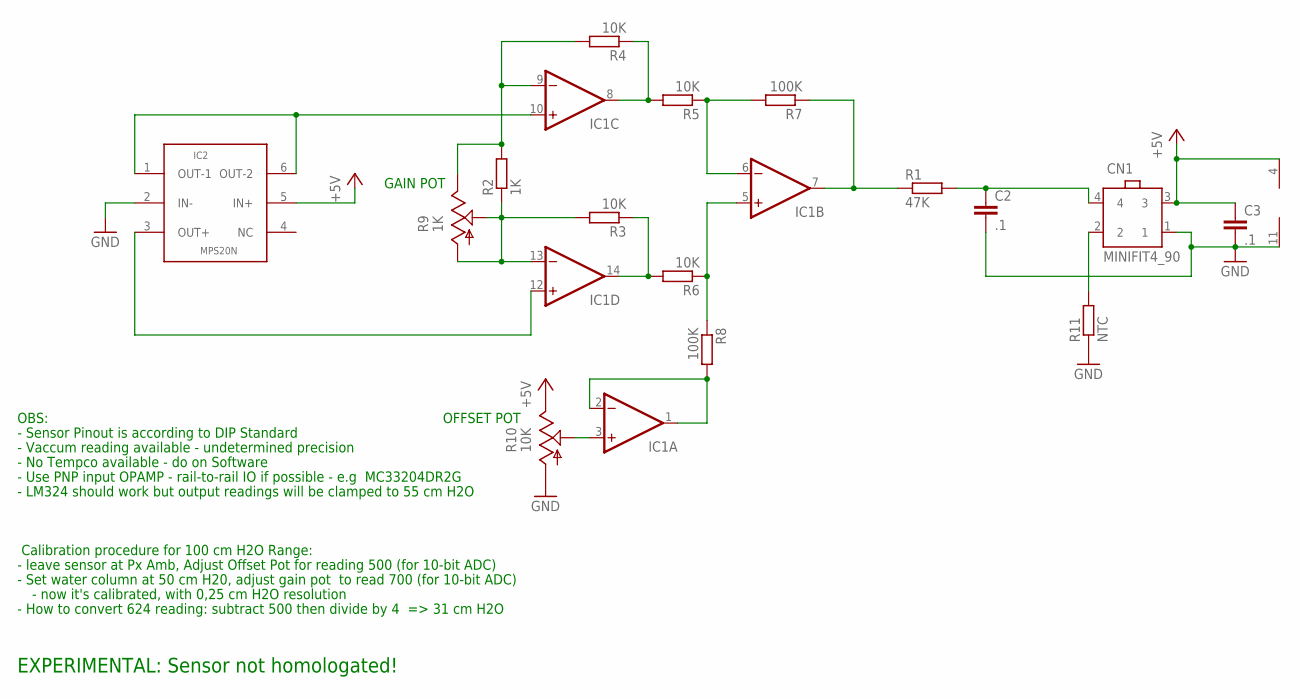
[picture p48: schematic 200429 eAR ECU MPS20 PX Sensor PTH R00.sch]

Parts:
C2, C3: .1; C050-025X075
CN1: MINIFIT4_90
IC1: LM324N; DIL14
IC2: MPS20N; DIL6-WIDE
R1: 47K; 0207/10
R2: 1K; 0207/10
R3, R4, R5, R6: 10K; 0207/10
R7, R8: 100K; 0207/10
R9: 1K; B64Y
R10: 10K; B64Y
R11: NTC; R0805W

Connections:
+5V: C3.1, CN1.3, IC1.4 (V+), IC2.5 (IN+), R10.E
GND: C2.2, C3.2, CN1.1, IC1.11 (V-), IC2.2 (IN-), R10.A, R11.1
unnamed: IC1.10 (+IN), IC2.1 (OUT-1), IC2.6 (OUT-2)
unnamed: C2.1, CN1.4, R1.2
unnamed: IC1.12 (+IN), IC2.3 (OUT+)
unnamed: IC1.9 (-IN), R2.2, R4.2, R9.E
unnamed: IC1.13 (-IN), R2.1, R3.2, R9.A, R9.S
unnamed: IC1.7 (OUT), R1.1, R7.1
unnamed: IC1.8 (OUT), R4.1, R5.2
unnamed: IC1.14 (OUT), R3.1, R6.2
unnamed: IC1.3 (+IN), R10.S
unnamed: IC1.6 (-IN), R5.1, R7.2
unnamed: IC1.5 (+IN), R6.1, R8.1
unnamed: CN1.2, R11.2
unnamed: IC1.1 (OUT), IC1.2 (-IN), R8.2

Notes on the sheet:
OBS:
Calibration procedure for 100 cm H2O Range:
- leave sensor at Px Amb, Adjust Offset Pot for reading 500 (for 10-bit ADC)
- Set water column at 50 cm H20, adjust gain pot to read 700 (for 10-bit ADC)
- now it's calibrated, with 0,25 cm H2O resolution
- How to convert 624 reading: subtract 500 then divide by 4 => 31 cm H2O
- Sensor Pinout is according to DIP Standard
GAIN POT
OFFSET POT
- Vaccum reading available - undetermined precision
- No Tempco available - do on Software
- Use PNP input OPAMP - rail-to-rail IO if possible - e.g MC33204DR2G
- LM324 should work but output readings will be clamped to 55 cm H2O
EXPERIMENTAL: Sensor not homologated!

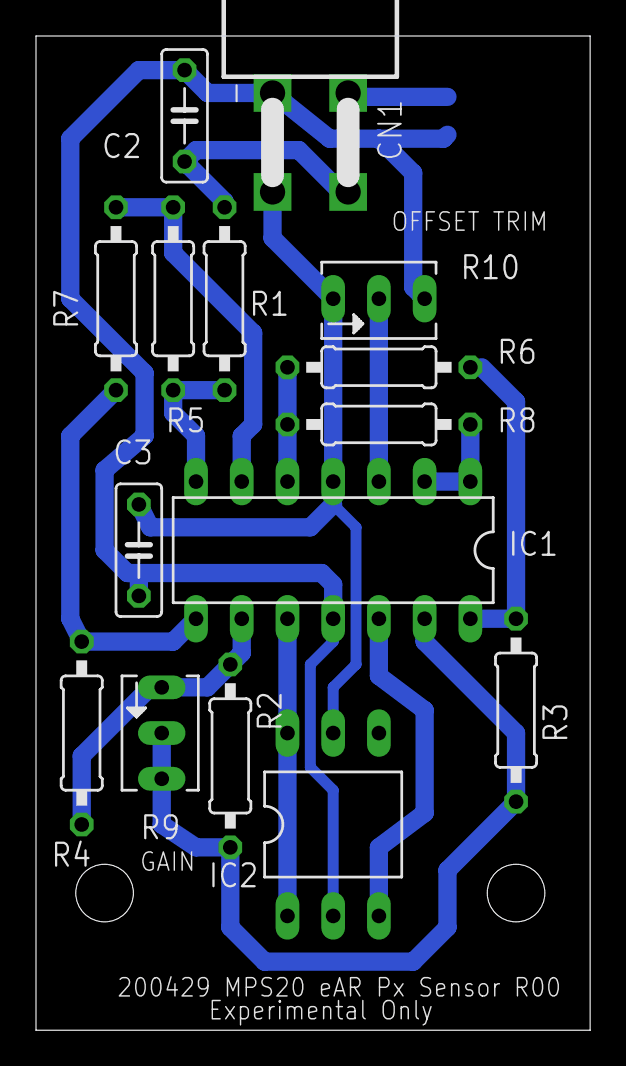
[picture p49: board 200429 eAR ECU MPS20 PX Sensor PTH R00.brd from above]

Board: 2 copper layers, 30.8 x 55.2 mm, 16 parts (1 on the bottom side), 15 nets.

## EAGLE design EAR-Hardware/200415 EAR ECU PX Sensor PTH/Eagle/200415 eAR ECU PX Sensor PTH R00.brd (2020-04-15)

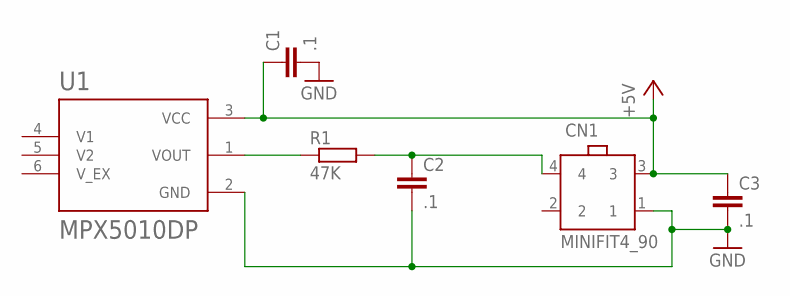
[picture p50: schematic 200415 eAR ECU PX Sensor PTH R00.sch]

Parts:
C1, C2, C3: .1; C050-025X075
CN1: MINIFIT4_90
R1: 47K; 0207/10
U1: MPX5010DP; XDCR_MPX5010DP

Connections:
+5V: C1.1, C3.1, CN1.3, U1.3 (VCC)
GND: C1.2, C2.2, C3.2, CN1.1, U1.2 (GND)
unnamed: C2.1, CN1.4, R1.2
unnamed: R1.1, U1.1 (VOUT)

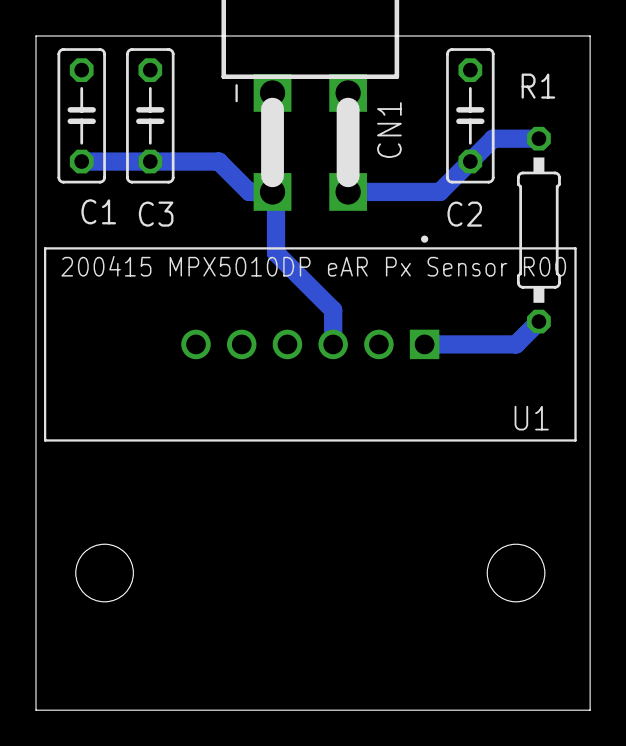
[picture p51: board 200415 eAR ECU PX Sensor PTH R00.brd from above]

Board: 2 copper layers, 30.8 x 37.5 mm, 6 parts (0 on the bottom side), 4 nets.

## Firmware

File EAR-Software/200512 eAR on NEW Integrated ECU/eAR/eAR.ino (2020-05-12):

/*
 * =====================================
 *              eAR Project
 *     Emergency Automatic Respirator
 *    Open Hardware Open Source Project
 * =====================================
 * Firmware Design started by Celso Monteiro in Apri 2, 2020 
 * Project target is to provide a simple ventilator system to help human breathing
 * Compiled by Arduino 1.8.5 for Arduino Pro Mini
 * FlexLed Serial Dump @57600 bps
 * ======================================================================================================================  
 * DISCLAIMER: we will NOT take any responsability on devices built using partial or total information from this project. 
 * Any device used for life support and medical applications must meet all local requirements 
 * and they must be homologated by local regulatory agencies in ANY case.
 * ======================================================================================================================  
 *  
 * Notes on HW and SW updates:
 * ===========================
 * - This project has a very tight schedule so some documents are not being updated as they should
 * - As this firmware has to be updated due to firmware improvement, we'll use it to keep HW info updated as well
 * - The HW related docs will be updated but not at the same time as this document.
 *  ===============================
 *  UPDATED Arduino Pro Mini Pinout
 *  ===============================
 *  TXO - TxD for Bootloader and FlexLed Serial Monitor (@57K6bps)
 *  RXI - RxD for Bootloader and FlexLed Serial Monitor
 *  RST - /Reset
 *  GND - GND
 *  D2 - reserved
 *  D3 - Latch 74HC165 Inputs for SPI Based Inputs expander. Level 0 for loading 1 for shifting IN
 *  D4 - Piezo self-osc Buzzer OUT - Active High
 *  D5 - BDC Motor PWM Hi-Side A - Provides 1 KHz PWM for Hi-side motor full bridge - Active High (CHANGED)
 *  D6 - BDC Motor PWM Hi-Side B - Provides 1 KHz PWM for Hi-side motor full bridge - Active High
 *  D7 - Multipurpose Red Led - Active High
 *  D8 - GPIO Motor Low Side A - Active High
 *  D9 - GPIO Motor Low Side B - Active High (CHANGED)
 *  D10 - Latch 74HC595 Outputs for SPI SPI Based Outputs expander. Rising edge transfer shift regiters to outputs
 *  D11 - MOSI for SPI based IO expander
 *  D12 - MISO for SPI based IO expander
 *  D13 - SCK for SPI based IO expander
 *  A0 - Analog readings for Pot1 - TIDAL VOLUME
 *  A1 - Analog readings for Pot2 - BPM (Breaths per Minute)
 *  A2 - Analog readings for Pot3 - Overpressure Threshold 
 *  A3 - Analog readings for Pot4 - Assisted Pressure Threshold (available only on Phase 2)
 *  A4 - Compression Arm Position Sensor (CHANGED)
 *  A5 - reserved (CHANGED)
 *  A6 - Analog readings of Pressure Sensor - MPX5010 or similar 10 KPa range Px sensor (0-5V output)
 *  A7 - Motor Shunt Current - 0.43V/A 
 *    - on mosfet Driver current will be limited to around 5A (2.15V)
 *    - on relay driver current will not be limited but it will be sensed until around 8 Amps, where it'll be clamped
 *  VCC - +5V provided by external +5V system voltage regulator
 *  RST - /Reset
 *  GND - GND
 *  RAW - Not connected
 *  
 *  SPI Based IO - IO1 Module - mandatory  - given names matches ULN2803 (outputs) and 74HC165 (inputs) nomenclature 
 *  
 *  EXP IO - INPUTS   
 *  ===============
 *  Inputs A-H are pulled-up, they are activated by connecting to GND, use NPN sensors or NO to GND.
 *  
 *  INPUT A - reserved for definition of Configuration (0) or Operation (1)
 *  INPUT B - reserved
 *  INPUT C - I/E ratio LSB \_ (Dip switch possible) CHANGED 00= 1:4  01= 1:3  10= 1:2 11= 1:1 (0= input opened 1= input GND) 
 *  INPUT D - I/E retio MSB / 
 *  
 *  INPUT E - T_Hold LSB \_ (Dip switch possible) CHANGED  00= 150ms  01= 250ms  10= 500ms 11= 1s  (0= input opened 1= input GND)
 *  INPUT F - T_Hold MSB /  
 *  
 *  INPUT G - 
 *  INPUT H - 
 *  
 *  EXP IO - OUTPUTS   
 *  ================
 *  ULN2803 outputs 1-8 are NPN type, you can connect directly 12V coil, T73 or auxiliary relays (e.g. to switch 24V or AC loads). 
 *  Simply connect the coil on +12V (same as system +12V PSU) and selected output. 
 *  Keep current to maximum 250mA per output and do NOT use 24V load directly because the ULN2803 diode pullups will connect the 24V load to PSU +12V
 *  
 *  OUTPUT 1 - reserved (not connected on ULN2003)
 *  OUTPUT 2 - 12V Automotive Siren for alarms
 *  OUTPUT 3 - 
 *  OUTPUT 4 - 
 *  OUTPUT 5 -
 *  OUTPUT 6 -
 *  OUTPUT 7 -
 *  OUTPUT 8 - 

 *  Notes on hardware:
 *  - the AMBU should be the one with the largest volume available. By using motor reversal, we can control AMBU compression displacement (Tidal Volume) on software
 *  - the BDC motor used for AMBU compression is a Mabuchi car window lift motor, left or right side
 *  - the Arm position sensor is a car tank float level sensor. Parameters are necessary:
 *    - EOC_UP (End Of Course Ambu Uncompressed)
 *    - EOC_Down (End of Course Ambu compressed at maximum)
 *    - recommended use of retundant normally open EOC, hall or switch type, slightly after EOC parameter limits 
 *  - there are 2 versions of motor drive; relays or mosfets
 *    - relay motor driver version uses T73 relays, available everywhere. Notes below: 
 *      - Use only LSA e LSB signals when using relays, PWM outputs HSA and HSB will NOT work
 *      - Inspiration speed will depend only on external voltage applied. Use a 5A (minimum) bench PSU with 47.000uF capacitor so PSU will not fail on motor start
 *      - Note that relay coil voltage should be obtained from CPU supply, before +5V regulator
 *    - mosfet drivers uses N-channel low level drive mosfets, or N-CH and P-CH mosfets, depending on version
 *      - N-CH mosfets should have Vgs of 2V or lower, Vds of 40V minimum and at least 15A continuos current. 
 *      - P-CH mosfets should have Vds of 40V minimum and at least 15A continuos current. 
 *    - The potentiometers are linear 10K type (1K-22K range are acceptable)
 *  

 ########################
    Revision History
 ########################

#R200402EAR01 - inverted pots or not ar now SW defined - depending on the pot travel
  - Default and recommended = Inverted pot

#R200403EAR01 - superloop timing is now interrupt driver - implemented by Flavio Alves based on original code by Jesse Tane

#R200403EAR02 - changes interrupt timing from 100ms to 10ms

#R200405EAR01 - adds motor mosfet drive, it IS now the standard drive, relay drive is too limited
  - adds PWM on High Side of Full bridge Motor Driver
  - problem with PWM, timer interrrupt interferes with PWM
    - Timer INT interferes with D9 adn D10
    - I was unable to make it work on D9 D10
    - D9 and D10 set to GPIO
    - D5 and D6 used for PWM on high side, analogWrite worked!
    - HARDWARE CHANGED on RELAY MODULE: SWAPPED LSB AND HSA pins on Arduino
    - FIRMWARE CHANGED on CPU MODULE: SWAPPED LSB AND HSA pins on Arduino
  - Relay driver treatment is the same, uses only Low Side lines LSA and LSB, unchanged
  - Mosfet Low Side Current limits now reduces Motor Peak Current
    - Ipk now limited to less than 5.5 Amps @99% PWM 12V with Capacitor Bank
    
#R200406EAR01 - adds motor absolute position based on car tank level sensor
#define ArmPosSns A5 // entrada leitura sensor posicao Motor
U16 ArmPosSensor;  // position sensor reading

#R200408EAR01 - Added pressure sensor on SW

#R200408EAR02 - Added GUI to Project
  - FlexLed changed output format for GUI interface
  - 10 Hz update rate, pre-processing is necessary due to Dumb GUI
  - Motor_phase replaced by Motor_Status
  - created new vars for setpoints and results

#R200408EAR03 - provides Fixed setpoints for frame generation only

#R200408EAR04 - HW change - swapped Arduino A4 and A5 functions due to an error on PCB layout V0 (single sided boards)
  - change requested by Diego Padilha 

#R200408EAR05 - Implements BPM as f(pot)

#R200408EAR06 - Implements generic error strategy
  - ErrorCount is incremented on each error found
  - ErrorID is programmed on specific error found

#R200408EAR07 - Implements TidalVolumeSet as f(pot)

#R200408EAR08 - Implements Final_Arm_Position as f(Course, TidalVolumeSet)
  - From now on, the final arm course is based on Tidal Volume Set

#R200409EAR01 - Processes breath timing based on stablished BPM

#R200409EAR02 - Calculates Ramping_Speed based on Processes breath timing 
 - TR is from 51 to 235 (30-8 BPM) assuming 150ms of Plateau_Hold_Time
 - Ramping_Speed=(TidalVolumeSet*8)/Ramping_Insp_Time; 
    - 8 is a mult constant used to increase resolution
 - Ramping_Speed values ranged from 6 (8 BPM - 200 ml TV) to 125 (30 BPM - 800 ml TV)
 
#R200409EAR03 - Calculates PWM based on Ramping_Speed  

#R200409EAR04 - Implements Task Time monitoring through Red_Led signal
- At this moment:
  - Common is taking 2.9ms
  - T0 is taking 0.005 ms
  - T1 is taking 3.8 ms
  - T2 is taking 0.080 ms
  - T3 is taking 0.006 ms
  - T4 is taking 0.006 to 0.035 ms
  - T5 is taking 0.005 ms
  - T6 is taking 0.800 ms
  - T7 is taking 0.350 to 0.450 ms
  - T8 is taking 0.800 ms
  - T9 is taking 1.2 ms
  
- T1 is reading pots, too critical, so the amazing (!) task of reading pots was divided on T1 and T2.
- This is the current situation:
  - Common is taking 2.9ms
  - T0 is taking 0.005 ms
  - T1 is taking 1.9 ms
  - T2 is taking 2 ms
  - T3 is taking 0.006 ms
  - T4 is taking 0.006 to 0.035 ms
  - T5 is taking 0.005 ms
  - T6 is taking 0.800 ms
  - T7 is taking 0.350 to 0.450 ms
  - T8 is taking 0.800 ms
  - T9 is taking 1.2 ms

- Results: Today WC is 50% ocupation

Target: 
- Common is about to grow significantly, so it can go up to 6ms (WC)
  - Tasks shoulgd be limited to 4 ms (WC)

#R200409EAR04 Implements operation with calculated timing and Ramps
- motor state machine moved out os scheduler, as planned
- Timer_Motor updated to 16-bit

Apr 9, 2020 - First funcional prerelease FW02 - Tidal Volume and BPM functional
Pressure limits not present

Apr 10, 2020 - Improved documentation
- included HW descripton on this firmware and definition of latest update.

Apr 10, 2020 - FIO2 controle removed from project scope.
It was removed because FIO2 Control could be independent of eAR system.
Even if we keep the concept of using 2 valves to control enriched air mix, 
it could be one FIO2 controller for several eAR systems.
So we can use an Arduino dedicated controller and 2 valves for all.
Just to register the concept:
There are 2 pneumatic valves: O2 and air valves
- O2 is always opened
- Air is cycled in 20-200 ms range every second, depending on potentiometer setpoint
- Both valves are stopped if intake bag is full. Bag full EOC signals that.
A calibration procedure is necessary to measure O2 and Air intake.
It could be simple as measure time to fill 2 separate bags. 
The bags are near atmosferic pressure, vinyl type if possible.
Example: 30 liter O2 bag and modulated 3 liter air bag fill at same time 
it would turn out to be 10:1 ratio or 91% oxygen

#R200410EAR01 Implement pressure limit based on OverPx Threshold Pot
- Adds motor cutoff in inspiration phase only
  - expiration was excluded because there could be a peak on exhaust valve opening
- Beep on OverPx created
- So now Overpressure behaviour could be described as:
  - On overpressure motor stops immediately
  - when motor stops, beeps starts and beep ends on start of next breathing cycle
- Operator then should do:
  - reduce Tidal volume or
  - reduce BPM (dP/dT will change) or
  - raise Overpressure limit
- results were repeatable and 1cm H20 resolution was accomplished
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

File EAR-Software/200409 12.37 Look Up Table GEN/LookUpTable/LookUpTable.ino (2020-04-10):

/*
 * LookUpTable Generator
 * Firmware Design by Celso Monteiro in April 9, 2020 
 *  Compiled by Arduino 1.8.5 for Arduino Pro Mini
 *  FlexLed Serial Dump @57600 bps
 *  
 *  Ramping_Speed values ranged from 6 (8 BPM - 200 ml TV) to 125 (30 BPM - 800 ml TV)
 */

// type definition
#define U8 unsigned char // define tipo unsigned char
#define U16 unsigned int
#define U32 unsigned long int

#define Speed_Start 6 // X1
#define Speed_End 125 // X2
#define PWM_Start 20  // Y1
#define PWM_End 90    // Y2

U8 Speed;
float A;
float B;
float PWM;

U8 DeltaX;
U8 DeltaY;
U16 Int_PWM;

// =====================
// =====================
//    INITIALIZATION
// =====================
// =====================

void setup()
{
  delay(100);
  Serial.begin(57600); // initialize serial interface for user interface - Serial Arduino Padrao
  Serial.println();
  Serial.println();

  // calculate linear relationship
  DeltaY=PWM_End-PWM_Start;
  DeltaX=Speed_End-Speed_Start;

  A=DeltaY;
  A=A/DeltaX;
  
  B=PWM_End-(A*Speed_End);

  Serial.print(" // LookUpTable GEN 1.0 - X Axis: Desired Speed, Y Axis: PWM -");

  Serial.print("  X1:");
  Serial.print(Speed_Start, DEC);  

  Serial.print("  X2:");
  Serial.print(Speed_End, DEC);  

  Serial.print("  Y1:");
  Serial.print(PWM_Start, DEC);  

  Serial.print("  Y2:");
  Serial.print(PWM_End, DEC);  

  Serial.print("  A:");
  Serial.print(A, 4);  

  Serial.print("  B:");
  Serial.print(B, 4);  
  Serial.println();

  Serial.print("const unsigned char PWM_Table [256] = {");
  Serial.println();
  
}

// =====================
// =====================
//       MAIN LOOP
// =====================
// =====================

void loop()
{
  for (Speed=0;Speed<255;Speed++)
  {
  PWM=A*Speed+B; 
  Serial.print(" ");
  Serial.print(PWM, 0);
  Serial.print(" , // ");
  Serial.print(Speed, DEC);
  Serial.println();
  delay (10);
  }

  PWM=A*Speed+B; 
  Serial.print(" ");
  Serial.print(PWM, 0);
  Serial.print("  // ");
  Serial.print(Speed, DEC);
  Serial.println();
  Serial.print(" };");  
  Serial.println();

for (;;);
} // end loop

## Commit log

2020-03-23 Atualização de RDSV Celso Monteiro
2020-03-23 Esboços movidos para pasta Hardware
2020-03-30 Add files via upload
    EAR ECU Boards: schematics and Gerbers for CPU, Expansion Board and Motor Driver-Relay Option
2020-03-30 Add files via upload
    3D visualization of boards, required Acrobat Reader DC
2020-04-03 Simple simulator for eAR ECU firmware development
    This simple simulator allows running EAR ECU basic functions:
    - reads pots as real ones
    - FlexLed (serial debug) is active and returns reasonable values for implemented functions
    - switched pot simulates flat motor current
    - motor machine status is shown
2020-04-03 First eAR ECU Prototype RUN
    Low resources POC worked! eAR ECU inclusive design is made on 3 single sided PCBs with shelf available PTH components connected by IDC connectors (same as old PCs) with retundant vias.
2020-04-03 Revisão inicial de arquitetura
    * Troca de diretório para funcionar no Arduino IDE
    * Inclusão de lib de escalonamento de tarefas
    * Ajuste do loop principal como atividade periodica
2020-04-03 Refatoração do timer
    Troca de lib
2020-04-05 eAR Mechanical prototype 3 Rocks!
    AMBU compressing torque is amazing. Motor speed meets 1 sec full stroke displacement with low voltage and current. Added (as planned) absolute position sensor based on car tank level sensor.
2020-04-05 eAR Mechanical Proto3 Operation Videos
    4V operation, unloaded AMBU compression, thanks Diego, Lucas for protos, Nicolai for hints
2020-04-06 eAR Mechanical Proto3 on PWM and Absolute Sensor
    New mosfet based PWM motor driver, absolute arm position sensor based on car tank sensor, working fine!
2020-04-07 Calibrating Pressure Sensor on H2O cm using H2O cm
    On your nearby hardware store you'll find all you need to build a simple H2O calibration system for your MEMS tubed pressure sensor. Relative pressure, of course. The second output, attached to an au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
2020-04-07 First Pressure Profile - Video and Scope waveforms
    Added Pressure Sensor MPX5010DP on eAR Pressure port. Best lung we could afford is a ballon. Same PWM profile as before. TEK images: on Top we have position sensor (Car Tank Float Sensor). Bottom is 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
2020-04-07 Added pressure sensor
2020-04-08 Real FlexLed Data for GUI testing purposes
    Same cycle as on previous movie, functional cycles during minutes. FlexLed serial dump was updated to present data for GUI under development. Position sensor is real, Tidal volume is simulated throug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
2020-04-08 eAR ECU - Motor Driver Mosfet NN version
    The Motor Driver - Mosfet NN version uses shelf N-CH low level drive mosfets to drive the motor. These mosfets are used in automotive applications so these semi are very common. Design by Gustavo Ort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
2020-04-10 FW02 prerelease
    Tidal, BPM and other functions working. Restriction on pressures not implemented. Open Loop PWM Lookup table implemented, not tuned. Automatic Lookup Table Generation will be released soon.
2020-04-10 LookUpTable Generator for PWM set as function of Desired Inspiration Ramping Speed.
    LookUpTable Generator for PWM set as function of Desired Inspiration Ramping Speed. It can be used to tune PWM response as a function of desired arm speed in inspiration. Open Loop - first aproach, i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
    It could be used as a generic LookUpTable generator for other purposes.
    As it was built using arduino IDE, there is no need for another compiler, so Arduino Pro Mini is the LookUpTable generator robot.
2020-04-10 eAR NEWS: Firmware controls Tidal Volume and BPM according to Set Potentiometers. First functional firmware
    eAR NEWS: Firmware controls Tidal Volume and BPM according to Set Potentiometers. First functional firmware produce variable pressure ramps as needed, FW met 8-30 BPM dynamic range specification.eAR
    Basic SDK: eAR ECU CPU + eAR ECU Mosfet Motor Driver + Car window Motor + fuel tank sensor as absolute position sensor+ mechanical body (to be published this week) + Arduino firmware FW02 + AMBU BAG
2020-04-10 eAR works now on limited Pressure, based on OverPx Threshold Pot
    On Inspiration Overpressure, eAR ECU shuts down motor and beeps. Repeatable results on 1 cm H2O resolution.
2020-04-11 Mechanical ARM for eAR - Design by Diego Padilha and Lucas Pianizzer
    Simple fully functional mechanical Arm for eAR ventilator system. It can be prototyped even on MDF. Besides nuts and bolts, only a car window motor and a car tank fuel sensor are necessary
2020-04-12 Motor Driver - Mosfet NN Version - Kicad Project with Gerbers
    The Motor Driver - Mosfet NN version now with Gerbers - Thanks to Diego Padilha!
    - uses shelf N-CH low level drive mosfets to drive the motor. PCB allows TO220, DPAK and D2PAK assembly. Mosfet basic requirements: N-Channel , gate threshold < 2.5V, Continuous drain current of 12A,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
    - These mosfets are used in automotive applications so these semi are very common. Design by Diego Padilha, Gustavo Ortenzi and C. Monteiro.
    - Added interface to absolute sensor to this board.
    - Pls notice that CPU signals have changed: We swapped LSB and HSA signals on this board. In CPU b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
2020-04-12 Added mechanical design files and Motor Driver - Mosfet NN version with gerbers
2020-04-12 Added External WatchDog Timer - Schematics, boards and Gerbers
    In order to achieve a reasonable level of reliability, a planned external watchdog was developed. Arduino bootloader is not compatible with watchdogs so this part needs to be removed when upgrading e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
2020-04-12 Added external watchdog support
    As planned, an external watchdog was added to eAR. Arduino is not reliable enough so this is a MANDATORY add-on. It is focused on restarting when arduino firmware loses control. Signals are generated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
2020-04-13 eAR WORKS! Functions meet MIT and MHRA specs!
    eAR is working on forced ventilation mode.
    - Specifications:
    - Tidal Volume SET: 200-800ml range, calibrated at 400ml
    - BPM SET: 8 to 32
    - I/E Ratio: 1:1, 1:2, 1:3 and 1:4
    - Plateau Hold Time: 150, 250, 500 and 1s
    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
2020-04-13 Added I/E and Plateau Hold Time programming, added Gol G3 tank level float sensor as absolute position sensor
2020-04-15 added Pressure Sensor Board
    The pressure sensor could be integrated in ECU Board but we preferred to have a three-wire cable instead of a long tube so we designed a new board connected to ECU by a 4-way Molex MiniFit Jr connect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
    [200415 eAR ECU PX Sensor PTH R00.GBL, 200415 eAR ECU PX Sensor PTH R00.GBO, 200415 eAR ECU PX Sensor PTH R00.GBP, 200415 eAR ECU PX Sensor PTH R00.GBS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]
2020-04-21 eAR Integrated ECU FR4 SMT
    eAR Integrated ECU = 10x10cm FR4 SMT board with CPU + EXP Board + Mosfet option Motor Driver + Hardware watchdog. UNVERIFIED.
2020-04-21 added FR4 Single PCB design for volume production and mech proto 3.2 with ball bearing
2020-04-21 included mass production possibility with FR4 SMT Board availability
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2020-04-22 eAR Compression Arm for AMBU - prototype 3.2 - functional
    Functional AMBU Compression Arm for eAR System R00. AKA Mech Prototype 3.2, added ball bearings on arm, works even on MDF parts. Uses Mabuchi BDC motor and Gol G3 Tank Float Sensor as absolute arm po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
2020-04-29 Added experimental Px Sensor Board based on MPS20N0040D Ultralow cost AVAILABLE sensor
    Added Pressure Sensor Board using EXPERIMENTAL MPS20N0040D Ultralow cost AVAILABLE sensor. This sensor is available from several sources in China for around 1 USD or less. All homologated sensors are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
    [200429 eAR ECU MPS20 PX Sensor PTH R00.GBL, 200429 eAR ECU MPS20 PX Sensor PTH R00.GBO, 200429 eAR ECU MPS20 PX Sensor PTH R00.GBP, 200429 eAR ECU MPS20 PX Sen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]
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2020-05-12 eAR ECU Integrated R01 - Minor Preproduction Changes - thanks to Diego Padilha
    eAR ECU Integrated R01 - Minor Preproduction Changes
    - Drilling corrections: Varistor, PPTC
    - Resistors: 22K and 47K changed to 100K, 4K7 changed to 10K
    - Bipolar transistors on H Bridge turned from BC807/BC817 to MMBT56 and MMBT06 to increase transient protection
    - Buzzer allow now 5 and 7.5mm pitch types
    - Potentiometers allow now 100 and 200 mils pitch types/models
    [Built-In Arduino Pro Mini.sch, Driver_MOSFET_NN.sch, EAR ECU Integrated_CPU_01-B_Cu.gbr, EAR ECU Integrated_CPU_01-B_Mask.gbr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]
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2020-05-20 EAR System Preliminary Bill of Materials
    EAR System Preliminary Bill of Materials - cost estimation of all components to build the AMBU compression system, including eAR ECU, Pressure Sensor and mechanical parts
    [200515 EAR SYSTEM BOM R00.xls]
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
